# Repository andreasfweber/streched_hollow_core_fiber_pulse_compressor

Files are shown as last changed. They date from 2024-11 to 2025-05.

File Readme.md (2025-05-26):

# Stretched hollow-core fiber pulse compressor
## A. Weber, H. Hampel, A. Grossek, M. Schultze, M. Ossiander

The compressor setup described was constructed as part of my bachelor's thesis at the Institute for Experimental Physics (IEP) of the TU Graz. The setup is similar to one constructed by Z. Pi, H. Y. Kim, and E. Goulielmakis and a pulse compressor that already perviously was constructed at the IEP by Hana Hampel.
>Z. Pi, H. Y. Kim, and E. Goulielmakis, "Petahertz-scale spectral broadening and few-cycle compression of Yb:KGW laser pulses in a pressurized, gas-filled hollow-core fiber," Opt. Lett. 47, 5865-5868 (2022)
 
It uses a high-pressure Ne-filled stretched hollow-core fused silica fiber to broaden the spectrum of a Yb:KGW Pharos laser (Light Conversion, center wavelength: 1030 nm, pulse duration: 150 fs, repetition rate: 6 kHz, average power: 6 W) via self-phase modulation. The Fourier limited pulse duration suggested by the output spectrum is 9 fs (intensity FWHM).

<p align="center">
  
  <br>
  <em>On the left hand side of this image, the vessel housing of the other compressor is visible.
Alongside to it is the stretched hollow-core fiber compressor, contained within a significantly
smaller vessel.</em>
</p>

<p align="center">
  
  <br>
  <em>Measured output spectra and transmitted power vs. neon pressure. The input power was ~5.5 W.</em>
</p>

<p align="center">
  
  <br>
  <em>Fourier transform limited pulse duration.</em>
</p>

# Pressure Vessel Considerations
The pressure vessel can withstand pressures up to 25 bar (with a safety factor of 2); the critical parts are the windows.
We use 2 mm-thick BK7 windows with a free aperture of 12 mm. Pressures exceeding 25 bar require a calculation to ensure the windows will withstand the pressure. Suitable formulas are, e.g., found here https://www.crystran.com/media/wysiwyg/Datasheets/design-of-pressure-windows_1.pdf.
 
An appropriate distance between the entrance and exit window and the entrance and exit of the fiber (focal point) prevents the laser from destroying the windows. For our laser setup, 45 cm work. This depends on the laser pulse parameters and focusing optics used.

In our first approach, we use Brewster angle windows to maximize transmission. Their handling is slightly harder than that of a window oriented perpendicular to the laser beam, due to an offset the beam experiences as it propagates through the glass. Both designs are functional; however, perpendicular windows with anti-reflective coatings have proven to be more practical and easier to implement. Owing to the broad spectral width, Brewster angle windows are still employed for the vessel's exit window to minimize reflection losses.

Additionally, we constructed slightly larger housings to accommodate aluminum extrusions with a greater diameter, as thinner profiles often exhibit deviations from straightness.

<p align="center">
  
  <br>
  <em>3D model of the pressure vessel.</em>
</p>

# Fiber Considerations
To improve coupling efficiency, it is important to match the beam waist radius (w) to the bore radius (a) of the fiber. The ideal beam waist can be calculated using the following formula: w ≈ 0.64 * a. 
>T. Nagy, P. Simon and L. Veisz, "High-energy few-cycle pulses: post-compression techniques", Advances in Physics: X, 6(1), 
https://doi.org/10.1080/23746149.2020.1845795, (2020)

The utilized fiber was a stretched molex TSP250794 (bore diameter: 250 μm, outer diameter: 794 μm, length: 1.1 m), which was mounted in an aluminum profile.

# Repository Structure
This repository contains equivalent drawings of the compressor in .stp and in .itp format (used by Autodesk Inventor). Each folder contains a file named "full_vessel," which contains the assembled structure. 

For more information, have a look at my bachelors thesis and feel free to ask questions. 

# License
The contents of the folders components_cc_stp and components_cc_itp are licensed under the terms of the CC BY 4.0 Creative Commons Attribution 4.0 International (full license: https://creativecommons.org/licenses/by/4.0/ ).

This open licensing does not apply to the CF components in the folders componetns_PfeifferVacuum_stp and components_PfeifferVacuum_itp which were provided by Pfeiffer Vacuum as .stp-models at https://vacuum-shop.com/shop/de_DE/ . We thank Pfeiffer Vacuum for allowing us to use their models.

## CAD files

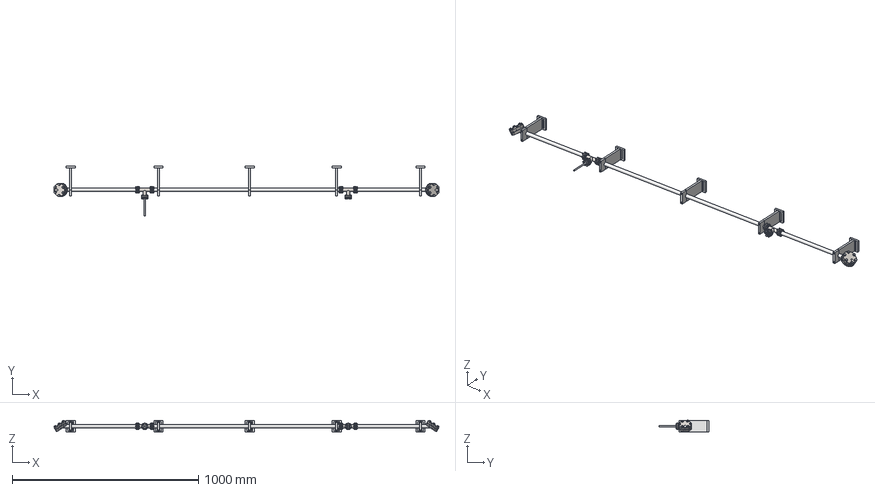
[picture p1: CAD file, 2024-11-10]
components_stp/full_vessel.stp
2064.9 x 266.2 x 63.2 mm
420FBL040
420FBL040-G
Schräges Rohr CF16
420RTS016
420FAN016-18 x 2
1mTube
Fuß Steher x 5
Steher oben Rohr x 5
Steher oben Rohr_1 x 5
420FBL016
blank_flange_CF40_MIR1
blank_flange_thread_CF40_MIR1
tube_Brewster_angle_MIR1
tee_CF16_MIR1
weld_flange_CF16_MIR1 x 2
420FBL016_1
Swagelok
420BSC016-20 x 36
420BSC040-20 x 12
Fenster Beam x 2
490DFL040-ID39-S10 x 2
490DFL016-S10 x 6
Fenster Kamera

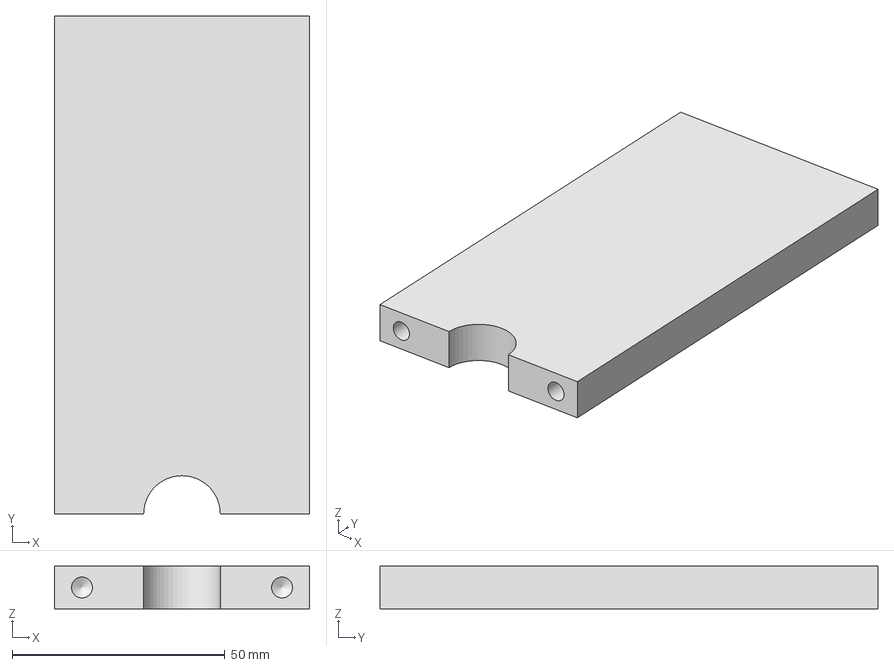
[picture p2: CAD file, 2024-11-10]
components_stp/components_cc_stp/post_bottom.stp
60.0 x 117.0 x 10.0 mm

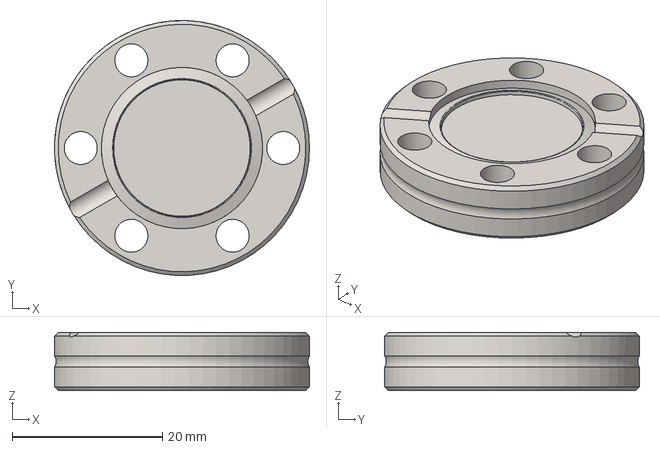
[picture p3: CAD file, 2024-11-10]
components_stp/componetns_PeifferVacuum_stp/blank_flange_CF16.stp
34.0 x 34.0 x 7.75 mm

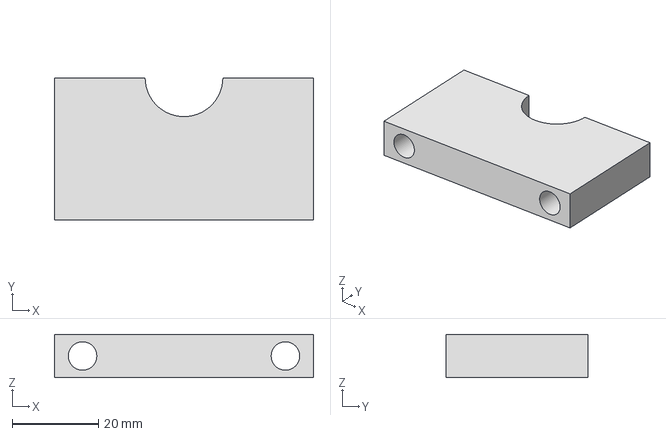
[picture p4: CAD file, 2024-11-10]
components_stp/components_cc_stp/post_top.stp
60.0 x 33.0 x 10.0 mm

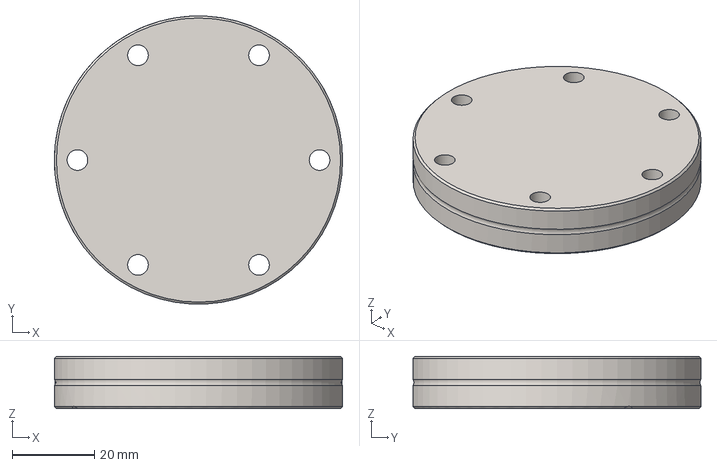
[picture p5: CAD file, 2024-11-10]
components_stp/componetns_PeifferVacuum_stp/blank_flange_thread_CF40_MIR1.stp
69.9 x 69.8 x 12.7 mm

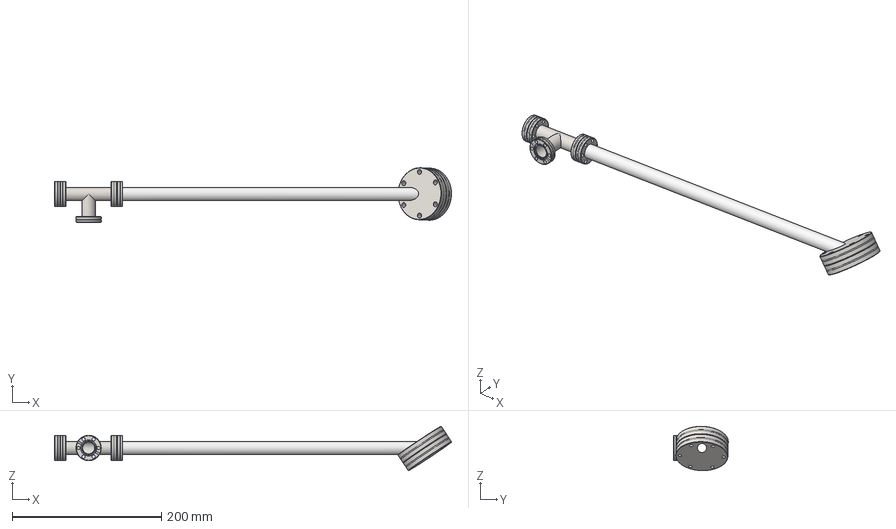
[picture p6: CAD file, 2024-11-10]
components_stp/components_cc_stp/window_and_tee_MIR1.stp
532.5 x 73.3 x 59.3 mm
blank_flange_CF40_MIR1
blank_flange_thread_CF40_MIR1
tube_Brewster_angle_MIR1
tee_CF16_MIR1
weld_flange_CF16_MIR1 x 2

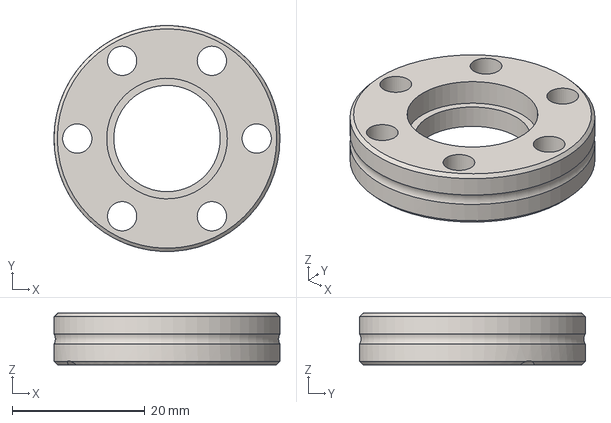
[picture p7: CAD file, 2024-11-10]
components_stp/componetns_PeifferVacuum_stp/weld_flange_CF16_MIR1.stp
34.0 x 34.0 x 7.75 mm

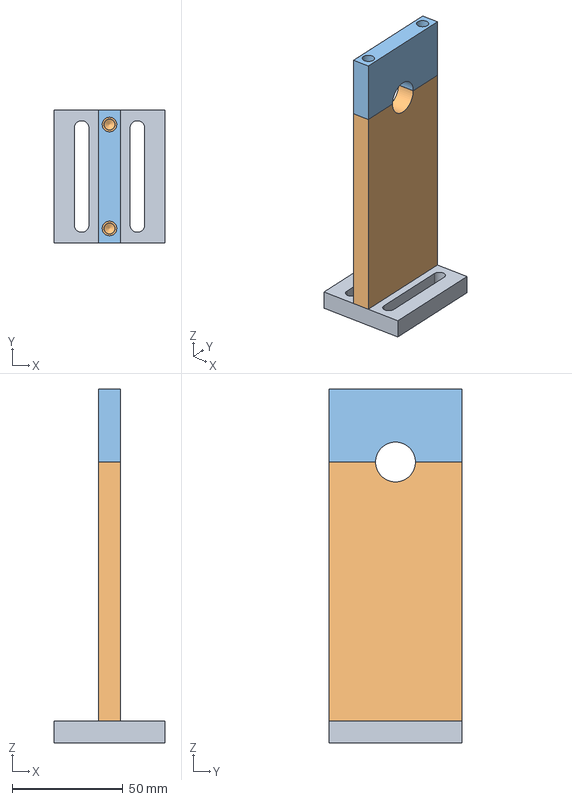
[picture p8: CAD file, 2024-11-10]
components_stp/components_cc_stp/post.stp
50.0 x 60.0 x 160.0 mm
Fuß Steher
Steher oben Rohr
Steher oben Rohr_1

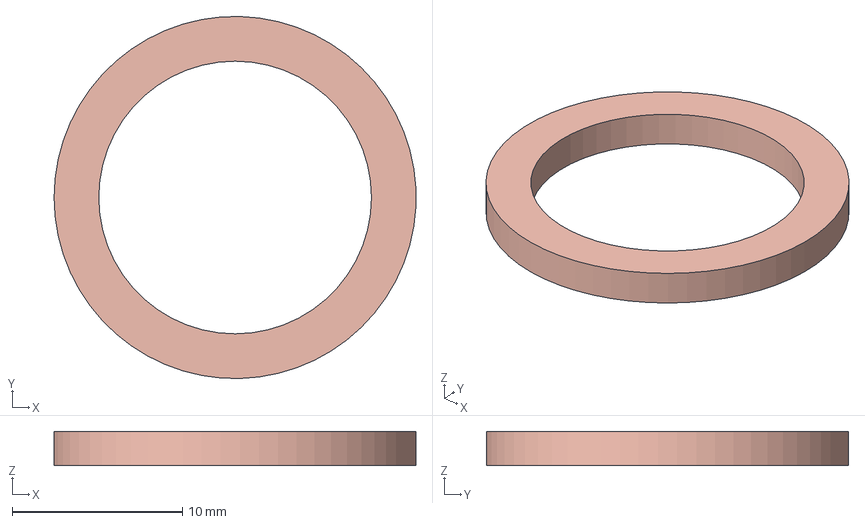
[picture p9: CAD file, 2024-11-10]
components_stp/componetns_PeifferVacuum_stp/gasket_CF16.stp
21.2 x 21.2 x 2.00 mm

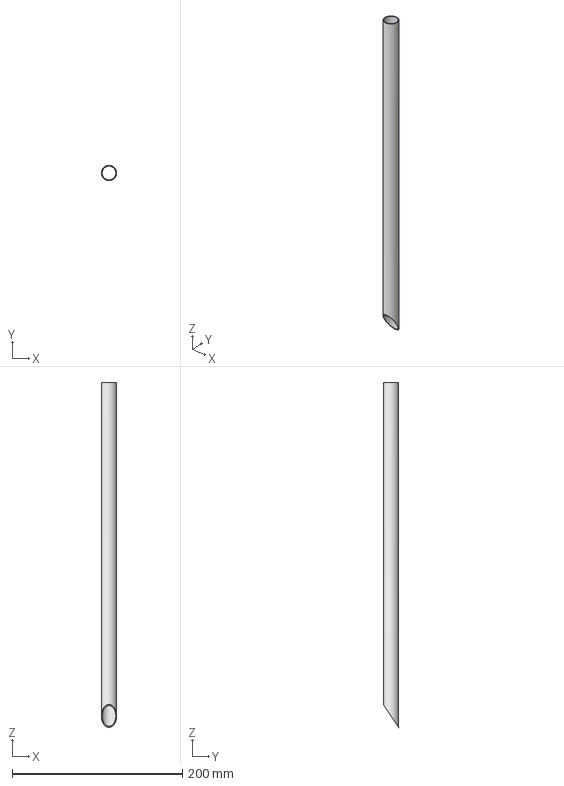
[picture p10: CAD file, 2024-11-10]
components_stp/components_cc_stp/tube_Brewster_angle.stp
18.0 x 18.0 x 405.0 mm

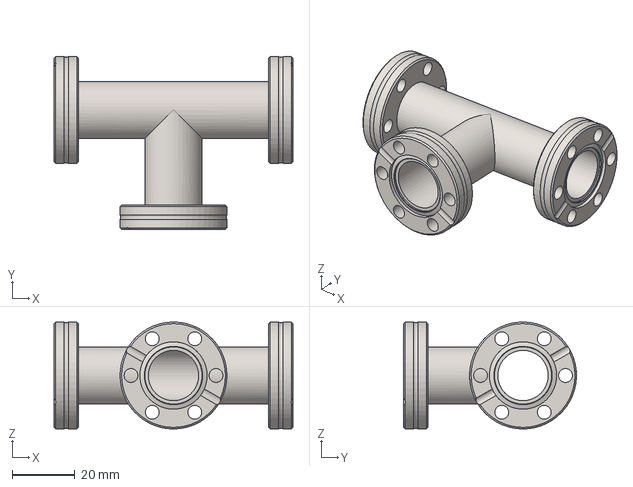
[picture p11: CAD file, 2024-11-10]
components_stp/componetns_PeifferVacuum_stp/tee_CF16_MIR1.stp
76.0 x 55.0 x 34.0 mm

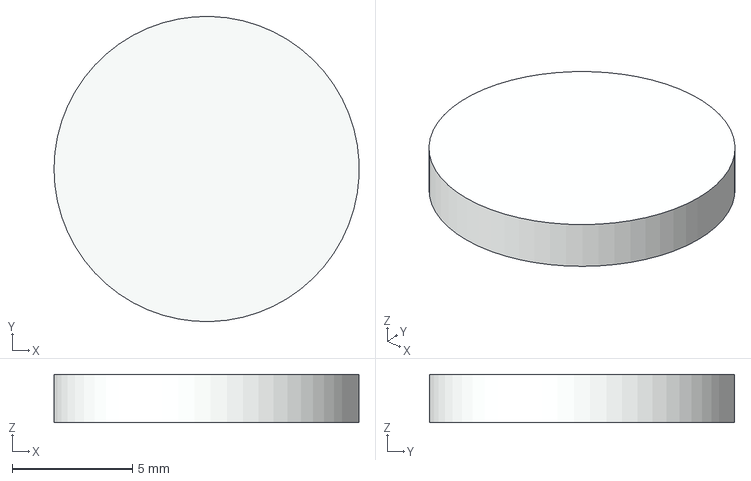
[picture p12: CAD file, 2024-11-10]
components_stp/components_cc_stp/window_camera.stp
12.7 x 12.7 x 2.00 mm

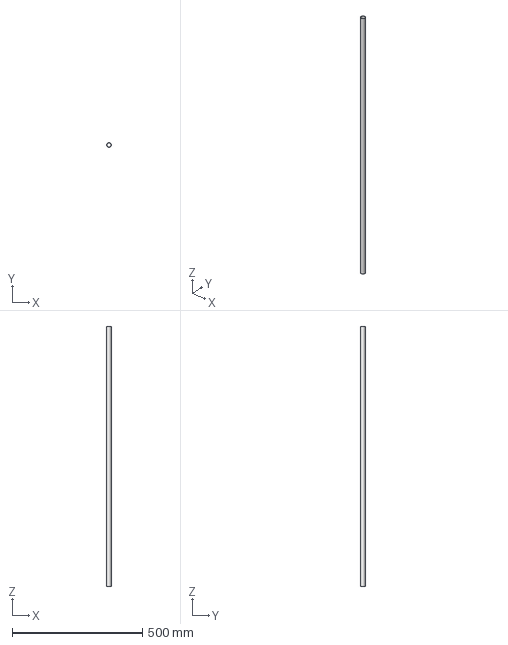
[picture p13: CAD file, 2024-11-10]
components_stp/components_cc_stp/tube_1m.stp
18.0 x 18.0 x 1000.0 mm

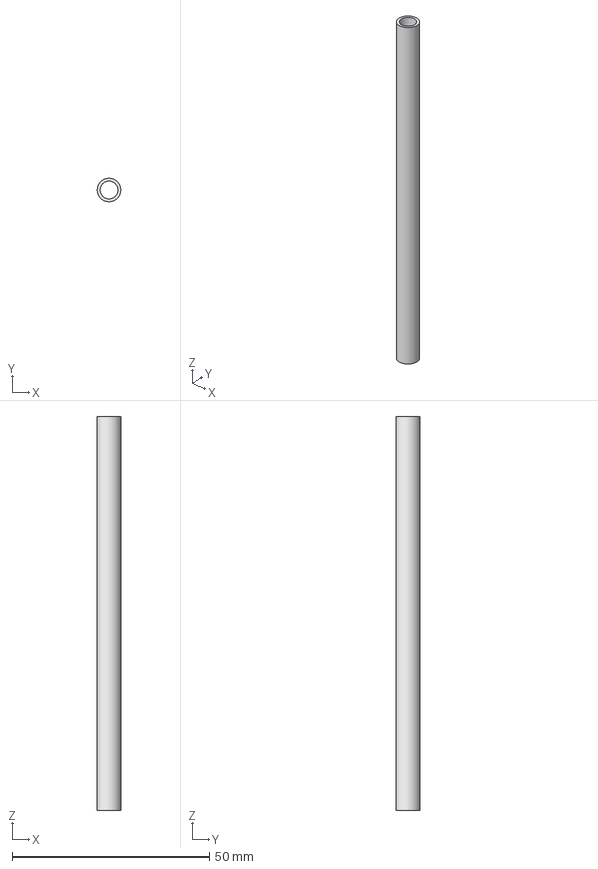
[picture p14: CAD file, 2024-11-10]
components_stp/components_cc_stp/Swagelok.stp
5.99 x 6.00 x 100.0 mm

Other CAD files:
components_stp/components_cc_stp/Flange_tube_MIR1.stp
components_stp/components_cc_stp/window_and_tee.stp
components_ipt/components_PfeifferVacuum_itp/blank_flange_CF16.ipt
components_ipt/components_PfeifferVacuum_itp/blank_flange_CF40.ipt
components_ipt/components_PfeifferVacuum_itp/blank_flange_CF40_MIR1.ipt
components_ipt/components_PfeifferVacuum_itp/blank_flange_thread_CF40.ipt
components_ipt/components_PfeifferVacuum_itp/blank_flange_thread_CF40_MIR1.ipt
components_ipt/components_PfeifferVacuum_itp/gasket_CF16.ipt
components_ipt/components_PfeifferVacuum_itp/gasket_CF40.ipt
components_ipt/components_PfeifferVacuum_itp/screw_ CF16.ipt
components_ipt/components_PfeifferVacuum_itp/screw_thread_CF40.ipt
components_ipt/components_PfeifferVacuum_itp/tee_CF16.ipt
components_ipt/components_PfeifferVacuum_itp/tee_CF16_MIR1.ipt
components_ipt/components_PfeifferVacuum_itp/tube_1m.ipt
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

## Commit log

2024-11-08 update components_itp
    [Flange_tube.0002.iam, Flange_tube.iam, Flange_tube_MIR1.iam, Swagelok.ipt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]
2024-11-10 removed components
    [Flange_tube.stp, Flange_tube_MIR1.stp, Swagelok.stp, blank_flange_CF16.stp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]
2024-11-21 update text
    [Flange_tube.0002.iam, blank_flange_CF40.0004.ipt, blank_flange_thread_CF40.0002.ipt, tee_CF16.0002.ipt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]
2024-11-22 structurral changes
    [Flange_tube.iam, Flange_tube.stp, Flange_tube_MIR1.iam, Flange_tube_MIR1.stp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]
